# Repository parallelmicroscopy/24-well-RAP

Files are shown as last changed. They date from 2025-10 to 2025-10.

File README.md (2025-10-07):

For an overview of the parallel microscopy project, start here: https://github.com/parallelmicroscopy/overview

For software, see: https://github.com/parallelmicroscopy/RAP-software

<b> Build instructions: </b>

This is a 24 well variant of the system described here: https://elifesciences.org/articles/56426.  The main differences are its inverted (parabolic reflector on the bottom).

<i> Things to keep in mind: </i>
- It uses 50 mm FL objective lenses, for a magnification of 2X. 
- It uses a combination of 3D printed parts and purchased optomechanics (1/2 inch steel posts + post holders).
- It is a 24 well imaging system (not a 96 well imaging system as described in the original publication). <i> The current design assumes the spacing of the wells is 18mm - please ensure that your 24 well plates have this exact spacing.</i>
- Image collection and LED control is through a PC or Mac computer (desktop or laptop).

<b> Construction tips: </b>

The system is build around a stack of 3D printed plates that hold the lenses, camera, and 24 well plate at user defined distances from each other and a parabolic reflector. The plates attach to 4 1/2 inch optical posts. A binder clip (https://www.staples.ca/collections/binder-clips-8639)  can be used to fix the position of any plate (they hold by friction). Most adjustments are done 'by hand' so <b>care must be taken to ensure that the following conditions are met</b>:

- The 50 mm FL objective lenses are 50mm beneath the 24 well plate.
- The camera sensor is 100 mm above the parabolic reflector.
- The camera is positioned directly above the center of the parabolic reflector.

The lenses and camera share a housing, so focus is achieved by moving the sample holder as the camera position is set by the focal length of the parabolic reflector. The current design includes an optional flexure stage and 50ml syringe which can be used to adjust the height of the sample holder (attach a second syringe to the first one to adjust the height of the sample), but this is not necessary. For a simpler, more stable, configuration: replace part 'g' by part 'a', which is sized to hold standard multiwell plates. You can use a leveling tool (e.g. https://www.thorlabs.com/thorproduct.cfm?partnumber=LVL03) to ensure the vertical plates are parallel to each other.


<br>
<b> 3D printed parts: </b>

The following pieces should be printed from PLA using a conventional 3D printer (e.g. Bambu X1 Carbon, or Prusa MK3).

a) 2 (or 3, see g below) x plate holder (with baffle to reduce stray light - a second lens holder without lenses)

b) parabolic mirror holder

c) 24 element lens array (plano-convex, 50mm focal length, 12.5 mm diameter, glass)

d) Periscope (two flat mirrors, 50mm x 125 mm, 3.1mm thick (float glass))

e) Lens holder with side attachment for the camera.

f) LED array holder with collimating lenses (10 mm diameter, 15 mm focal length, clear plastic)

g and h) *optional* flexure stage for focus control: alternatively print an extra plate holder (part 'a')

<b>Camera:</b>

The camera used in the current configuration is an Allied Vision Alvium 1800 U-052m:

https://www.edmundoptics.ca/p/allied-vision-alvium-1800-u-052m-117-05mp-c-mount-usb-31-monochrome-camera/48246/

The camera is a 7.3 × 5.6 mm square CMOS sensor mounted in a <b>CS</b> housing (CS-mount   flange focal distance (FFD) = 12.526 mm, and the outer diameter of the cylindrical lens mount is 1 inch ). A camera with a <b>CS-mount</b> housing is needed for this system as a conventional 'C' mount blocks light at oblique angles. Alternatively you can remove the camera housing altogether, but if you do so add a small cooling fan near the camera (https://www.digikey.ca/en/products/detail/adafruit-industries-llc/4468/11587354) to disipate heat. 

<b> Optics:</b>

Parabolic reflector: <b>1</b> x https://www.edmundoptics.ca/p/220mm-dia-x-100mm-fl-alum-coated-parabolic-reflector/23405/

50 mm FL 12.5 mm diameter plano-convex lenses: <b>24</b> x  https://www.edmundoptics.ca/p/37796/38881/

flat 50x125 mirrors: <b>2</b> x https://www.edmundoptics.ca/p/50-x-125mm-4-6lambda-mirror/2310/

Optional: In addition, illumination uniformity can be improved by using plastic collimating lenses between the LED array at the sample.: e.g. https://www.aliexpress.com/i/32545080396.html (- the lenses can be removed from their holders and placed in 3D printed part 'f' above).

<b> LED array: </b>

The array consists of 24 Dotstar LEDs (LEDs: https://www.adafruit.com/product/2343) positioned on a grid with 18mm pitch.
The LED array was custom built and assembled by PCBway (at a cost of about 35$ per array with 5 array minumum order).  <i>Gerber files are available on request</i>.

Alternatively, a commercially available LED array can be used e.g. https://www.adafruit.com/product/1430. But be aware that there are a few disadvantages. i) First, the LED spacing doesn't exactly match (there will be a slight shift noticable near the edge of the multiwell plate); ii) The commercial array also uses slower pixels with different wiring and timing requirements (Neopixels); iii) The Arduino control software would need to be altered to account for the diffent pixel number (every second pixel would be used) and pixel architecture. The software uses the FastLED.h (https://github.com/FastLED/FastLED) library so the changes would be relatively simple. Its worthwhile noting that the original publication used Neopixel array (https://elifesciences.org/articles/56426), and it was effective.

<b> LED array control: </b>

The LEDs used in the array are Dotstar 3 color LEDs. They can be controlled by a standard Arduino Uno microcontroller.

https://store-usa.arduino.cc/products/arduino-uno-rev3?srsltid=AfmBOopXxBkr__GUeiH5OznG9X-kM2l1Z6z6UYeTNxjmHn4hPxC6iHAW

<i>Please note that if you purchase an Arduino compatible microcontroller instead of the official one above, you may have to edit the software to ensure that its recognized.</i>

<b> Commercial optomechanics: </b>

In addition to the 3D printed parts, you will need <b>1/2 inch optical posts, post holders and hardware</b>:

2 x Ø12.7 mm Optical Post, L = 300 mm: https://www.thorlabs.com/thorproduct.cfm?partnumber=TR300/M

4 x Ø12.7 mm Optical Post, L = 250 mm: https://www.thorlabs.com/thorproduct.cfm?partnumber=TR250/M

4 x Ø12.7 mm Optical Post, L = 50 mm: https://www.thorlabs.com/thorproduct.cfm?partnumber=TR50/M

8 x Right-Angle Clamp for Ø1/2" Posts: https://www.thorlabs.com/thorproduct.cfm?partnumber=RA90/M

1x 150 mm x 300 mm Aluminum Breadboard: https://www.thorlabs.com/thorproduct.cfm?partnumber=MB1530/M

and M6 screws, e.g.: https://www.thorlabs.com/thorproduct.cfm?partnumber=SH6MS20

<b> Cables: </b>

Allied Vision recommends the following cables for their camera:

1) A USB 3 cable connects the camera to the PC: https://www.digikey.ca/en/products/detail/allied-vision-inc/12327/12083506
  
2) A trigger cable connects the Arduino to the camera: https://www.digikey.ca/en/products/detail/allied-vision-inc/12322/11200629

   <i>Pin 2</i> from the trigger cable should be connected to <i>Arduino pin 10</i>,  and <i>pin 6</i> from the trigger cable should be connected to <i>Arduino ground.</i>

Less expensive versions of the above cables also work in our experience.

**Finally** ... keep in mind that the hardware and software for this project are actively being worked on. Please contact [gil.bub@mcgill.ca](mailto:gil.bub@mcgill.ca) prior to starting your build for last-minute construction tips.

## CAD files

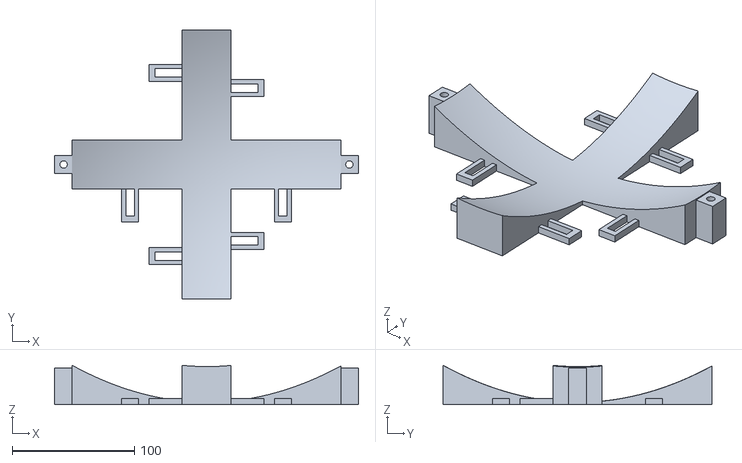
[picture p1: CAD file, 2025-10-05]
alberta_base.stl
249.0 x 220.0 x 32.3

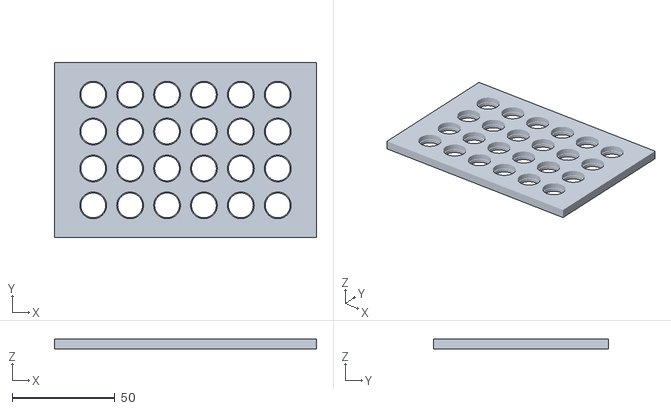
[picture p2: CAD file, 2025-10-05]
alberta_lens_holder.stl
127.8 x 85.5 x 5.00

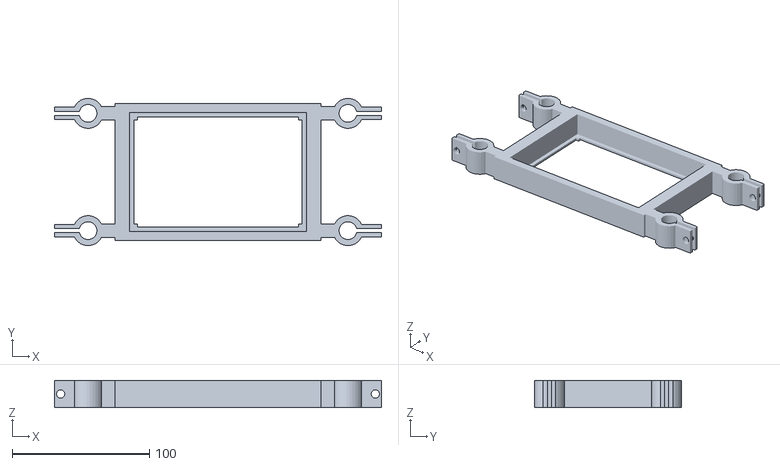
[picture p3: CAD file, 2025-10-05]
alberta_plate_holder.stl
238.3 x 107.3 x 20.0

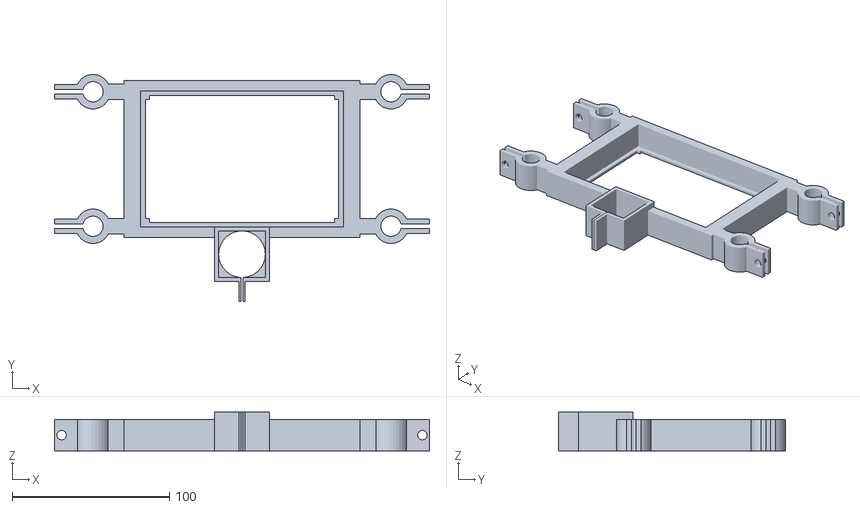
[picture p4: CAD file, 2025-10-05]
alberta_cam2.stl
238.3 x 144.1 x 24.6

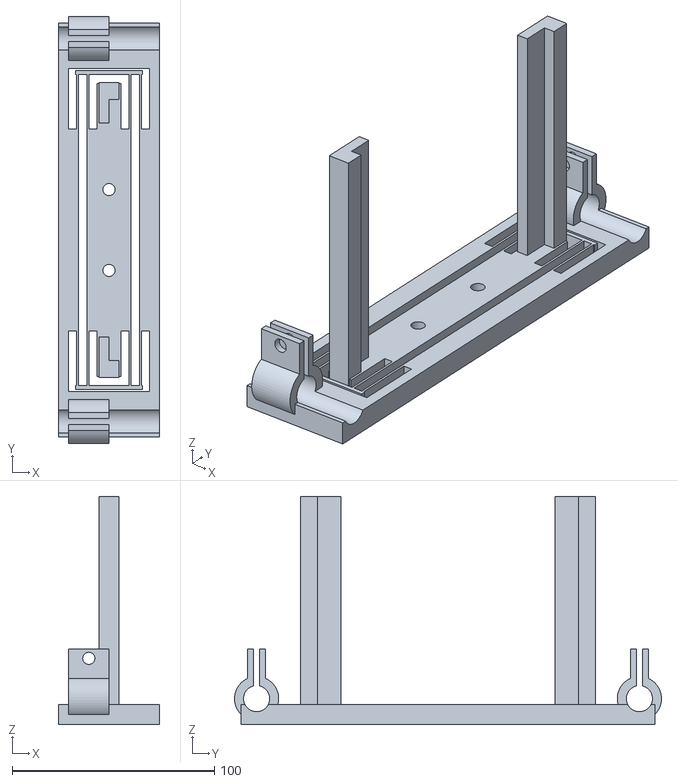
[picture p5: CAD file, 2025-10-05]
alberta_flexture_back_v3.stl
50.0 x 211.3 x 113.0

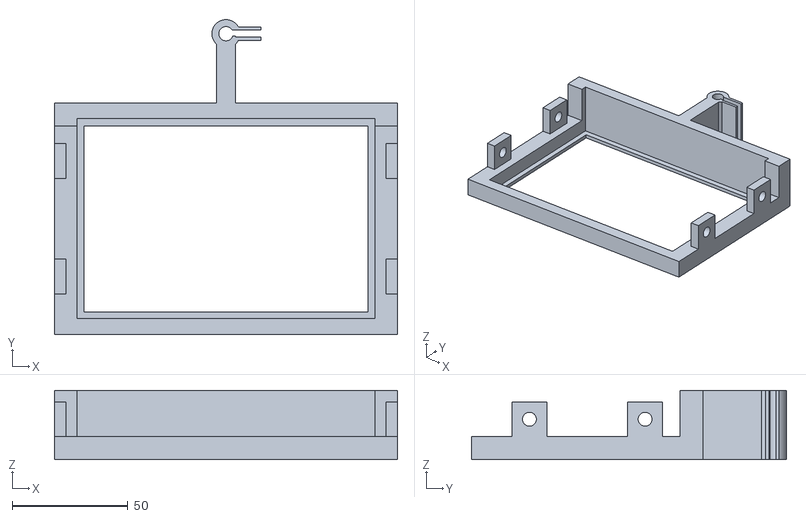
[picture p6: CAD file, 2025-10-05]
alberta_plate_adjuster3.stl
148.3 x 136.1 x 30.0

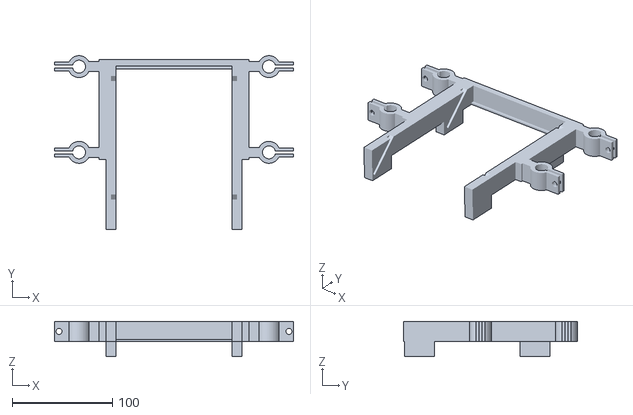
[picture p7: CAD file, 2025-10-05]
alberta_periscope_low.stl
238.3 x 173.2 x 35.0

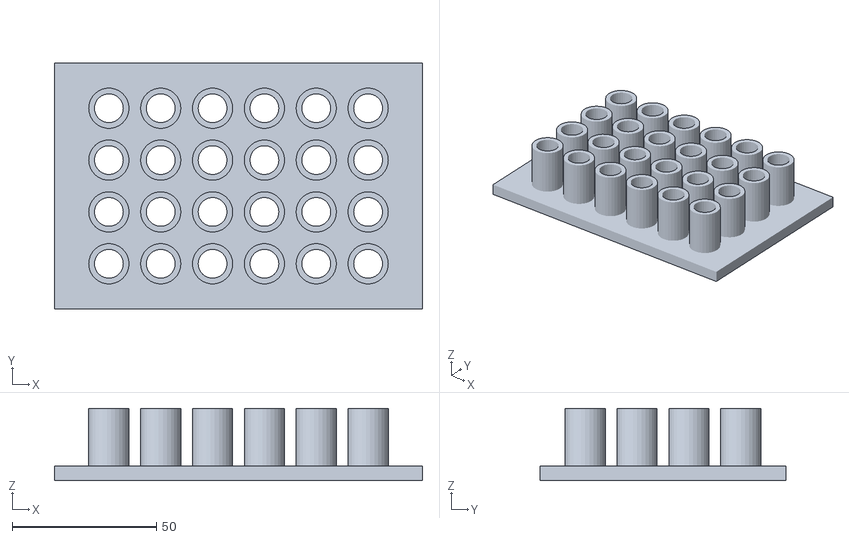
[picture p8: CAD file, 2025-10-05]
alberta_led_holder.stl
127.8 x 85.5 x 25.0

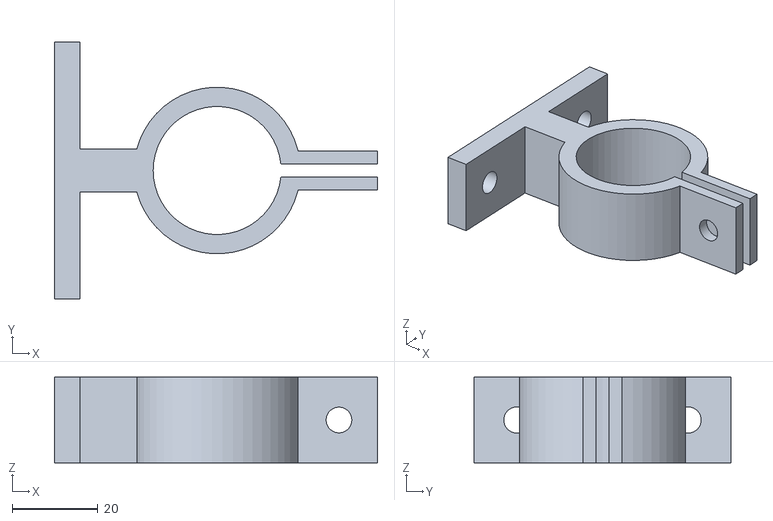
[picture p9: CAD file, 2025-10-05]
alberta_fb_syringe_clamp.stl
75.5 x 60.0 x 20.0

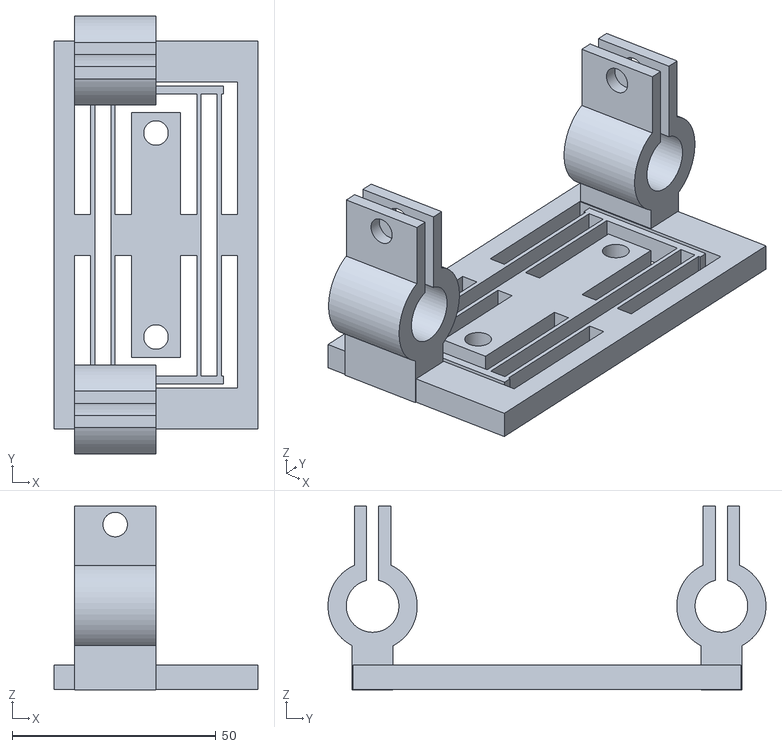
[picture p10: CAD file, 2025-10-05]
alberta_flexture4.stl
50.0 x 107.3 x 45.0

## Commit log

2025-10-05 Flexture clamp
    [alberta_flexture4.stl]
2025-10-05 STLs for the RAP microscope
    [alberta_base.stl, alberta_cam2.stl, alberta_fb_syringe_clamp.stl, alberta_flexture_back_v3.stl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]
